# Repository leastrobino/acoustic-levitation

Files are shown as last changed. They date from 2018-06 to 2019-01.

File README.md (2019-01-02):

# Acoustic levitation

An acoustic levitation device designed as a daughterboard for the [DE0-Nano-SoC](http://www.terasic.com.tw/cgi-bin/page/archive.pl?Language=English&CategoryNo=165&No=941) (Terasic Inc.)

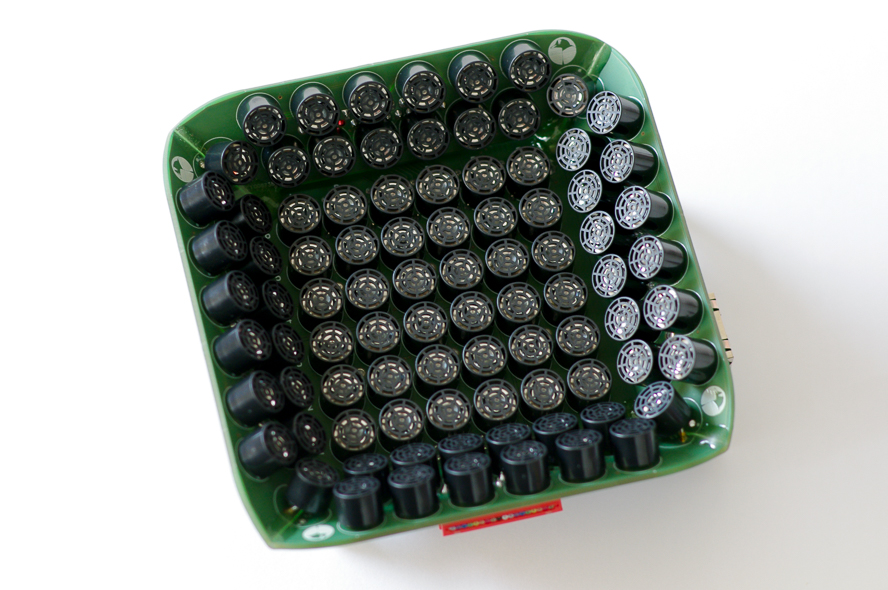
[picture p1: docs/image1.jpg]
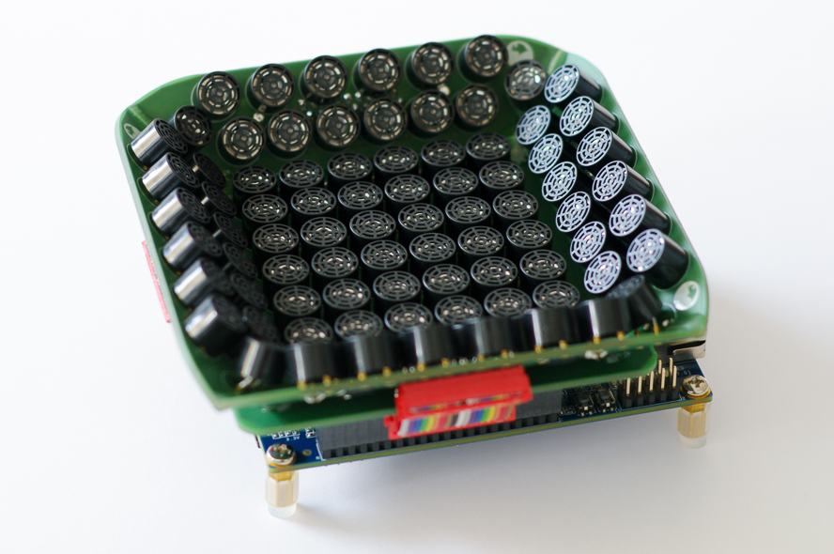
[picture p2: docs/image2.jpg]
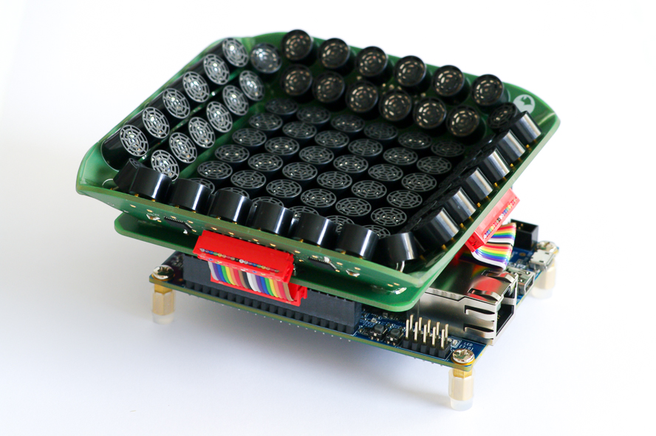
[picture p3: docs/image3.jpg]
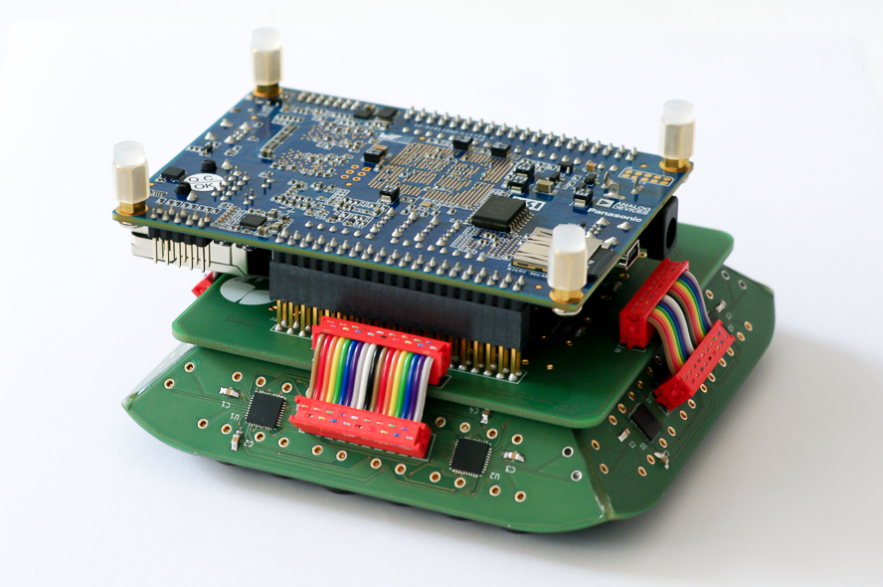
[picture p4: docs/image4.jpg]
[](https://leastrobino.github.io/acoustic-levitation/image1.jpg)[](https://leastrobino.github.io/acoustic-levitation/image2.jpg)[](https://leastrobino.github.io/acoustic-levitation/image3.jpg)[](https://leastrobino.github.io/acoustic-levitation/image4.jpg)

The piezoelectric transducers signals generation is written in VHDL. The phases computation and the G-Code interpreter are written in C and run on embedded Linux. The device controls 88 channels at 40 kHz with a phase resolution of π/625.

## Demonstration videos

#### Levitation of a 3 mm EPS particle in hand
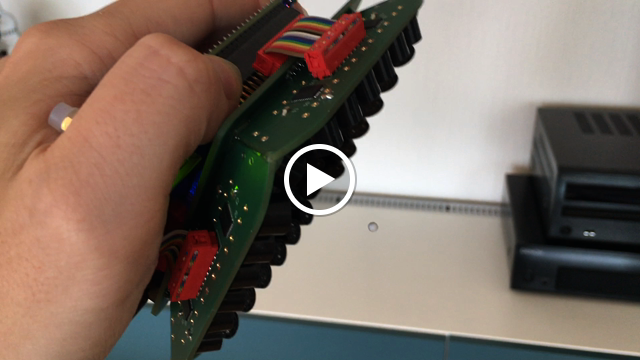
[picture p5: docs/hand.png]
Levitation device in hand


#### Up and down movements using G-Code
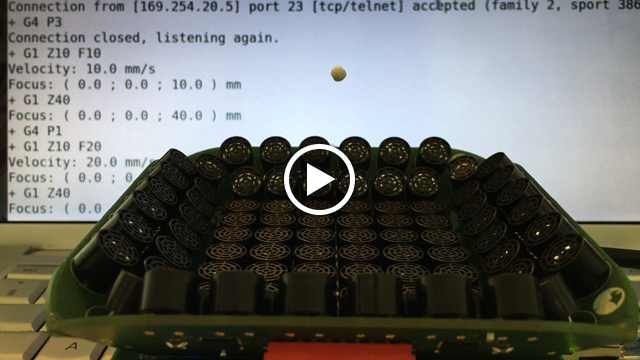
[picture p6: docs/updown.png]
Up and down movements


#### 2 mm EPS particle following a toolpath exported from FlatCAM
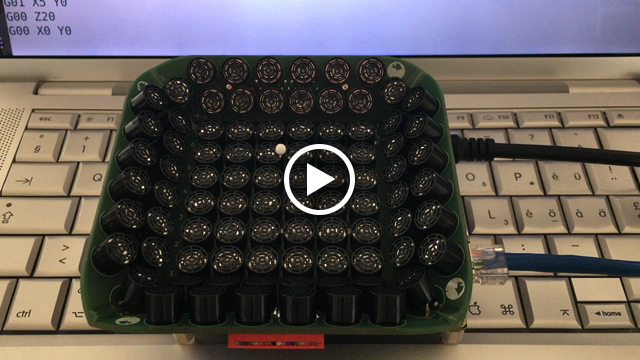
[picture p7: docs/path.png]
Particule following a path


Toolpath:

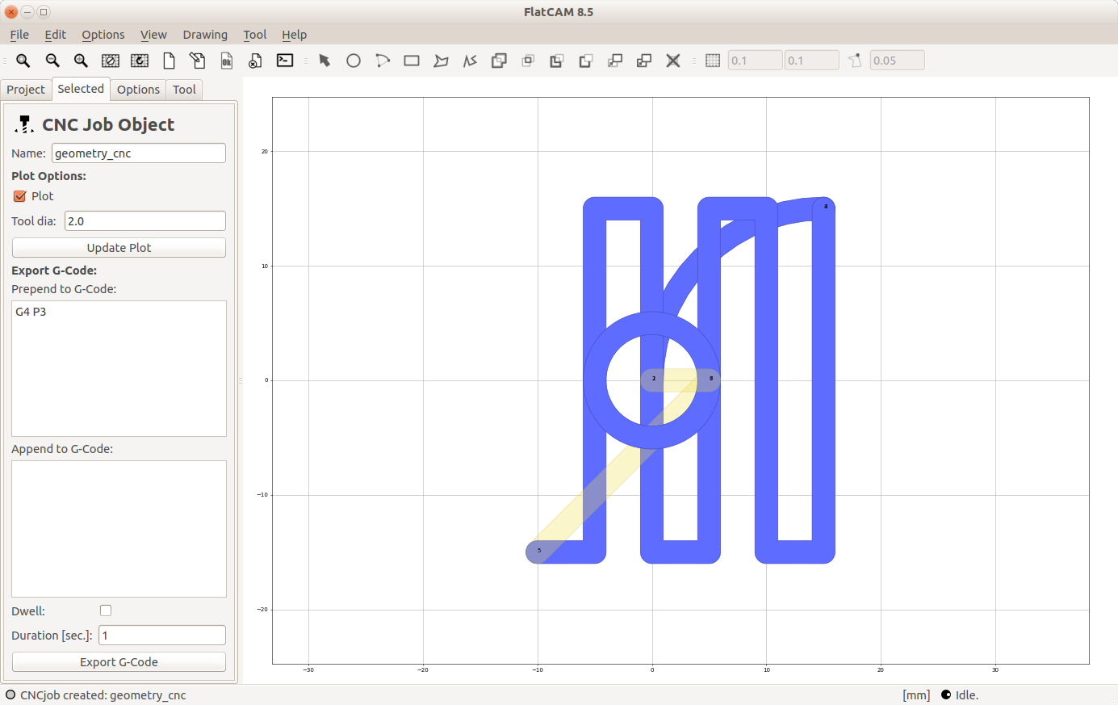
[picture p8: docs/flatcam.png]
Toolpath in FlatCAM
[](https://leastrobino.github.io/acoustic-levitation/flatcam.png)

## Bill of materials

| Quantity | Manufacturer           | Part number     |
| :------: | :--------------------- | :-------------- |
| 1        | CUI Inc.               | PJ-102AH        |
| 14       | Maxim Integrated       | MAX17079GTL+    |
| 88       | Murata                 | MA40S4S         |
| 2        | Samtec Inc.            | SSW-120-03-G-D  |
| 8        | TE Connectivity        | 8-215079-8      |
| 8        | TE Connectivity        | 8-215083-8      |
| 176      | TE Connectivity        | 8134-HC-8P2     |
| 1        | Traco Power            | TSR 2-2450      |
| 1        | Vishay Siliconix       | SI3421DV-T1-GE3 |
| 1        | Wurth Electronics Inc. | 61300111121     |
| 1        | Wurth Electronics Inc. | 61300811121     |
| 1        | Wurth Electronics Inc. | 61301011121     |
| 28       | Wurth Electronics Inc. | 885012207072    |

The PCBs were manufactured by [Eurocircuits](https://www.eurocircuits.com) (class 6D).

## License

This project is licensed under the [CERN OHL v1.2](LICENSE).

## References

1. A. Marzo, S. A. Seah, B. W. Drinkwater, D. R. Sahoo, B. Long, and S. Subramanian, *Holographic acoustic elements for manipulation of levitated objects*, Nature Communications 6, 8661, 2015.  
   <https://www.nature.com/articles/ncomms9661>
2. A. Marzo, *GauntLev: A Wearable to Manipulate Free-floating Objects*, Proceedings of the 2016 CHI Conference on Human Factors in Computing Systems (CHI '16), 3277-3281, 2016.  
   <https://dl.acm.org/citation.cfm?id=2858370>
3. A. Marzo, M. Caleap, and B. W. Drinkwater, *Acoustic Virtual Vortices with Tunable Orbital Angular Momentum for Trapping of Mie Particles*, Phys. Rev. Lett. 120, 044301, 2018.  
   <https://journals.aps.org/prl/abstract/10.1103/PhysRevLett.120.044301>
4. A. Künstner, *Lévitation acoustique*, Bachelor thesis, hepia, University of Applied Sciences Western Switzerland (HES-SO), Geneva, Switzerland, 2017.

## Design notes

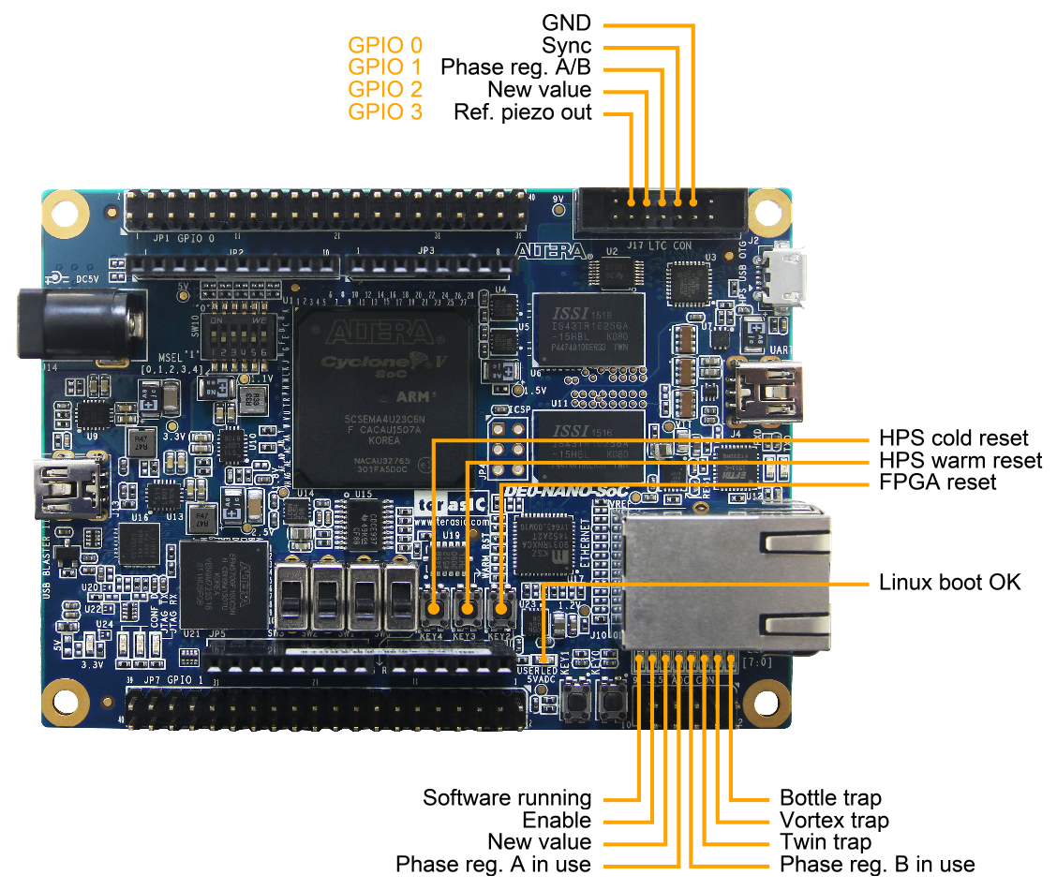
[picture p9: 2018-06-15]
docs/DE0-Nano-SoC_GPIO_LED_Buttons.png

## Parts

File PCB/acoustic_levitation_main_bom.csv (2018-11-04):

% Source: /Users/Lea/Documents/Acoustic levitation/PCB/acoustic_levitation_main.sch
% Date: Saturday, 03 November 2018 at 16:48:32
% Component count: 66
Reference | Quantity | Value | Footprint | Manufacturer | Manufacturer part number | Supplier 1 | Supplier part number 1 | Supplier 2 | Supplier part number 2
C1, C2, C3, C4, C5, C6, C7, C8, C9, C10, C11, C12 | 12 | 100n | C_0805_HandSoldering | Wurth Electronics Inc. | 885012207072 | Digi-Key | 732-8061-1-ND
J1 | 1 | DE0-Nano-SoC: GPIO 0 | Socket_Strip_Straight_2x20_Pitch2.54mm | Samtec Inc. | SSW-120-03-G-D | Digi-Key | SAM11959-ND
J2 | 1 | DE0-Nano-SoC: GPIO 1 | Socket_Strip_Straight_2x20_Pitch2.54mm | Samtec Inc. | SSW-120-03-G-D | Digi-Key | SAM11959-ND
J3 | 1 | DE0-Nano-SoC: JP3 | Pin_Header_Straight_1x08_Pitch2.54mm | Wurth Electronics Inc. | 61300811121 | Digi-Key | 732-5321-ND | Distrelec | 300-93-649
J4 | 1 | DE0-Nano-SoC: JP2 | Pin_Header_Straight_1x10_Pitch2.54mm | Wurth Electronics Inc. | 61301011121 | Digi-Key | 732-2670-ND | Distrelec | 300-93-651
J5 | 1 | DE0-Nano-SoC: JP5[3] | Pin_Header_Straight_1x01_Pitch2.54mm | Wurth Electronics Inc. | 61300111121 | Digi-Key | 732-5314-ND | Distrelec | 300-93-642
J6, J7, J8, J9 | 4 | 8-215079-8 | TE_8-215079-8 | TE Connectivity AMP Connectors | 8-215079-8 | Digi-Key | A99466CT-ND
J10 | 1 | PJ-102AH | CUI_PJ-102AH | CUI Inc. | PJ-102AH | Digi-Key | CP-102AH-ND
Q1 | 1 | Si3421DV | TSOP-6_2.9x1.5mm_Pitch0.95mm | Vishay Siliconix | SI3421DV-T1-GE3 | Digi-Key | SI3421DV-T1-GE3CT-ND
TR1, TR2, TR3, TR4, TR5, TR6, TR7, TR8, TR9, TR10, TR11, TR12, TR13, TR14, TR15, TR16, TR17, TR18, TR19, TR20, TR21, TR22, TR23, TR24, TR25, TR26, TR27, TR28, TR29, TR30, TR31, TR32, TR33, TR34, TR35, TR36 | 36 | MA40S4S | Murata_MA40S4S_TE_8134-HC-8P2 | Murata | MA40S4S | Digi-Key | 490-7707-ND
U1, U2, U3, U4, U5, U6 | 6 | MAX17079 | QFN-40-1EP_6x6mm_Pitch0.5mm_HandSoldering | Maxim Integrated | MAX17079GTL+ | Digi-Key | MAX17079GTL+-ND
U7 | 1 | TSR2-2450 | Traco_TSR2 | Traco Power | TSR 2-2450 | Mouser | 495-TSR2-2450 | Distrelec | 300-67-301

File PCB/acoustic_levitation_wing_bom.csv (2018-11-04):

% Source: /Users/Lea/Documents/Acoustic levitation/PCB/acoustic_levitation_wing.sch
% Date: Saturday, 03 November 2018 at 16:48:45
% Component count: 21
Reference | Quantity | Value | Footprint | Manufacturer | Manufacturer part number | Supplier 1 | Supplier part number 1 | Supplier 2 | Supplier part number 2
C1, C2, C3, C4 | 4 | 100n | C_0805_HandSoldering | Wurth Electronics Inc. | 885012207072 | Digi-Key | 732-8061-1-ND
J1 | 1 | 8-215079-8 | TE_8-215079-8 | TE Connectivity AMP Connectors | 8-215079-8 | Digi-Key | A99466CT-ND
TR1, TR2, TR3, TR4, TR5, TR6, TR7, TR8, TR9, TR10, TR11, TR12, TR13, TR14 | 14 | MA40S4S | Murata_MA40S4S_TE_8134-HC-8P2 | Murata | MA40S4S | Digi-Key | 490-7707-ND
U1, U2 | 2 | MAX17079 | QFN-40-1EP_6x6mm_Pitch0.5mm_HandSoldering | Maxim Integrated | MAX17079GTL+ | Digi-Key | MAX17079GTL+-ND

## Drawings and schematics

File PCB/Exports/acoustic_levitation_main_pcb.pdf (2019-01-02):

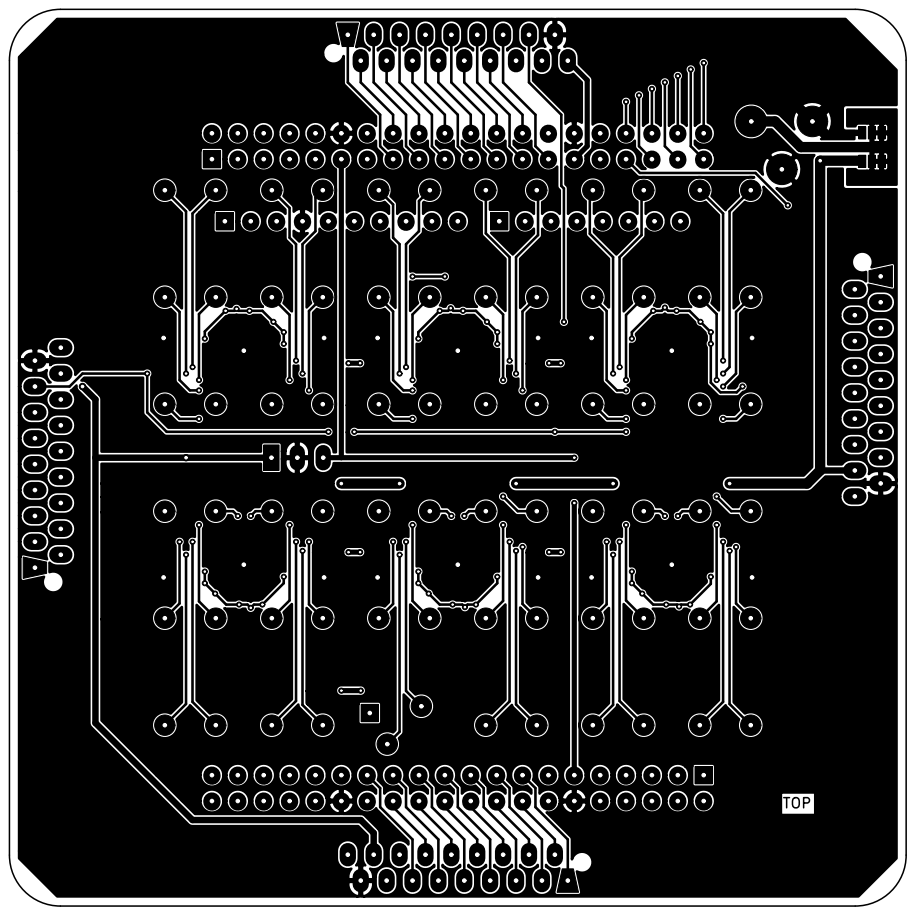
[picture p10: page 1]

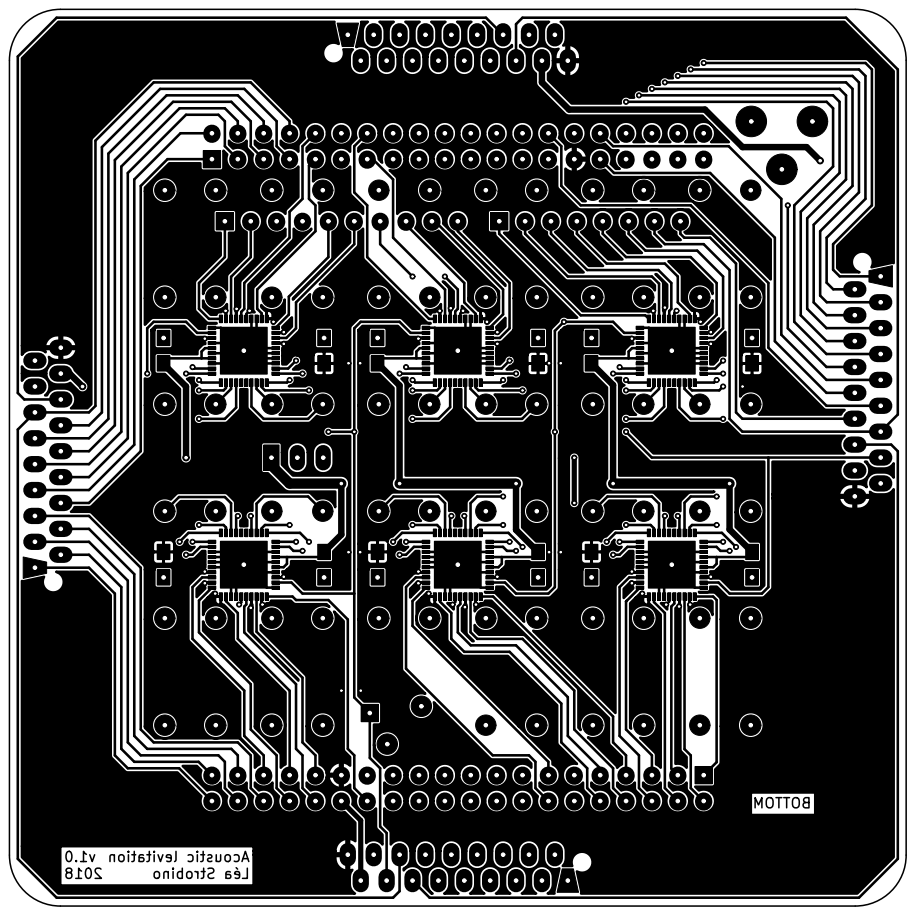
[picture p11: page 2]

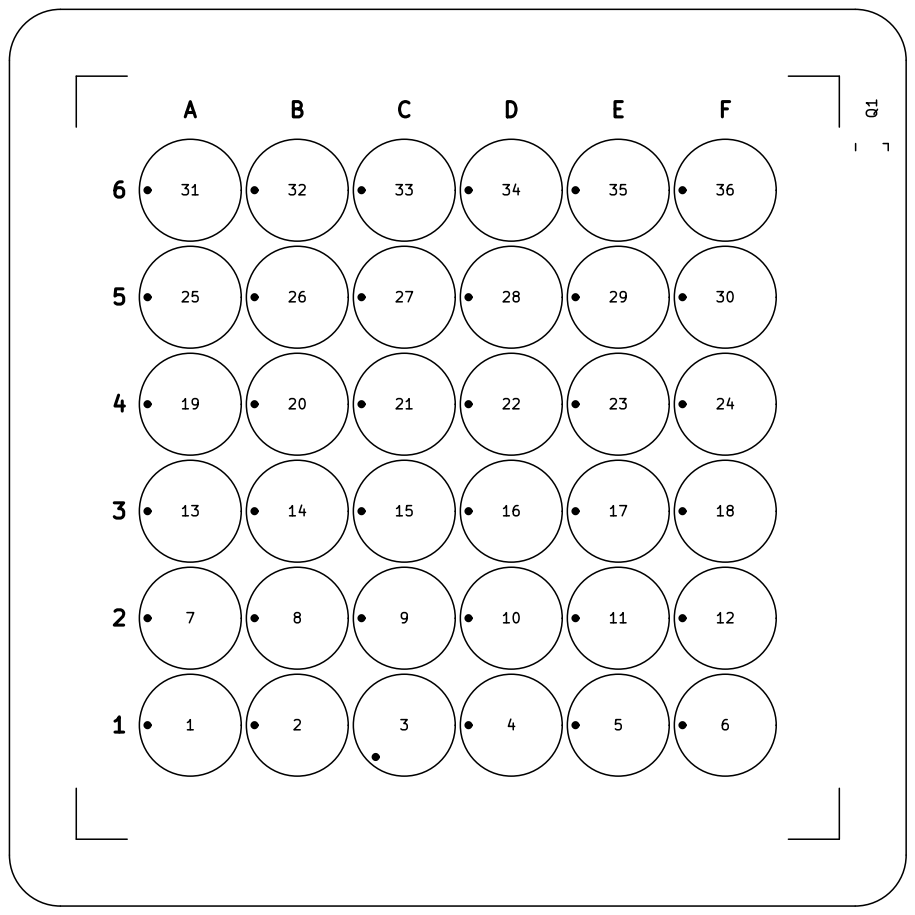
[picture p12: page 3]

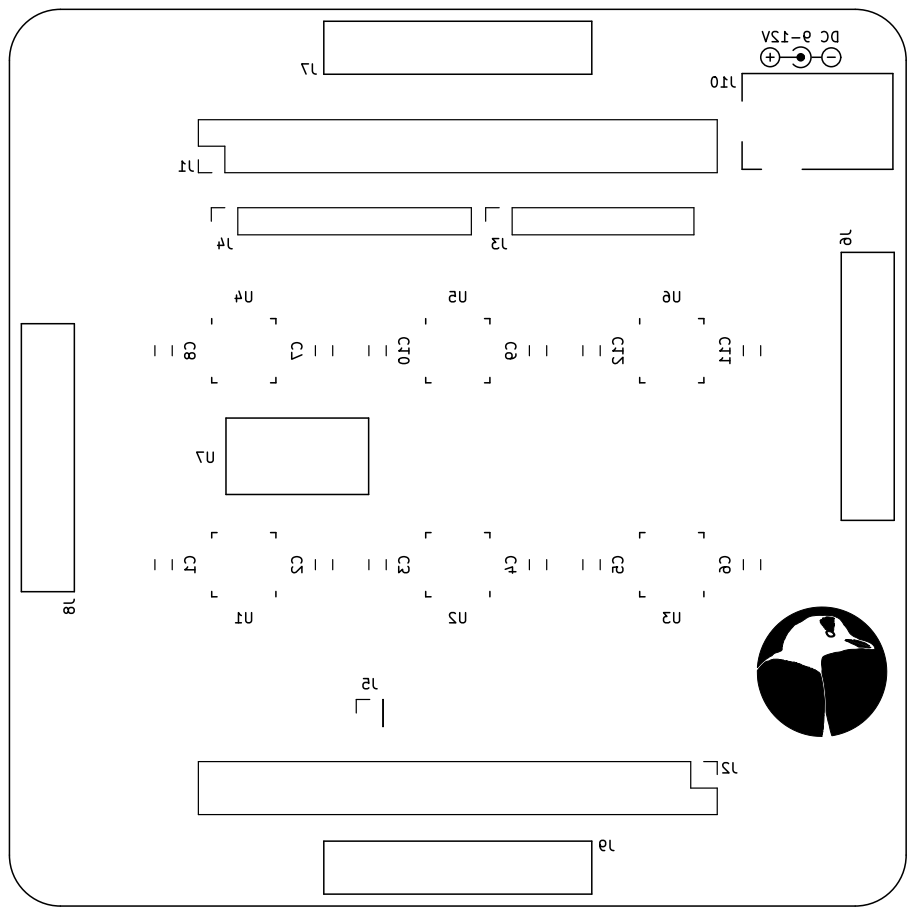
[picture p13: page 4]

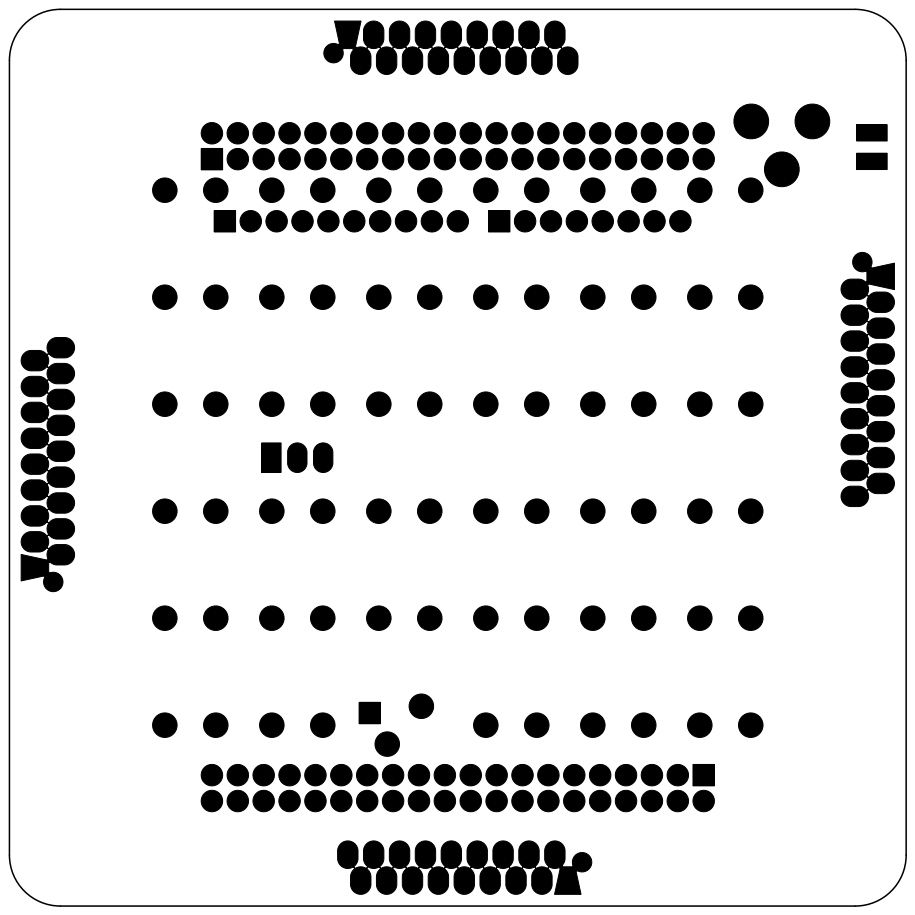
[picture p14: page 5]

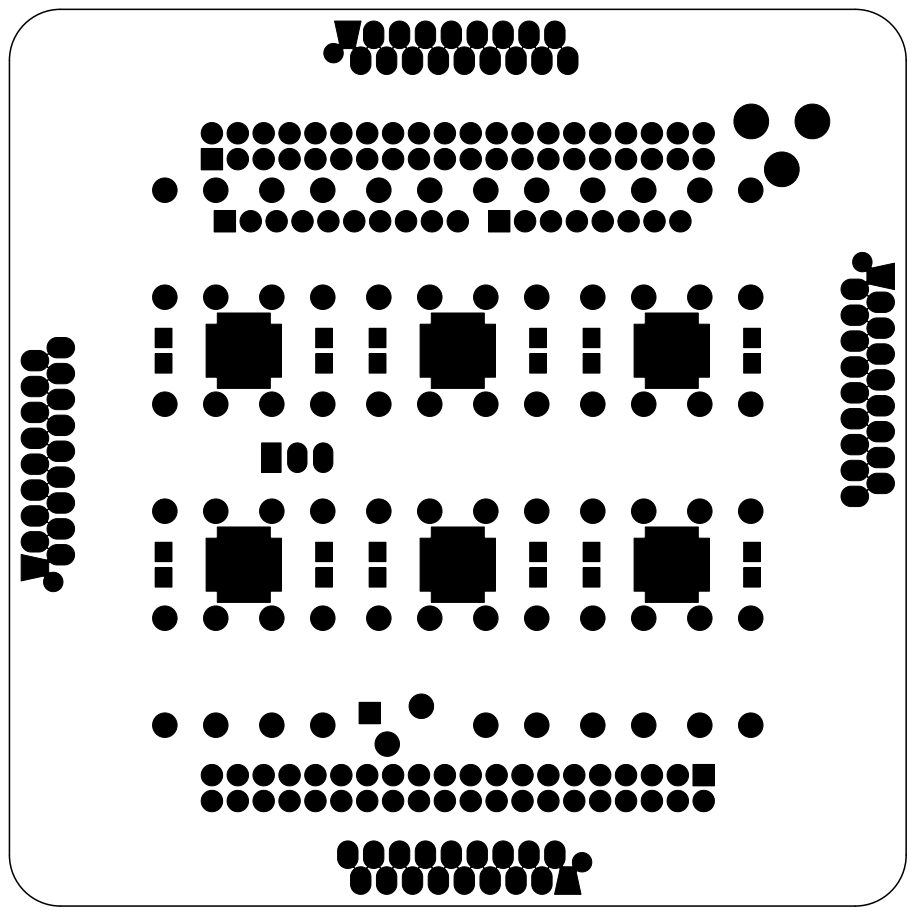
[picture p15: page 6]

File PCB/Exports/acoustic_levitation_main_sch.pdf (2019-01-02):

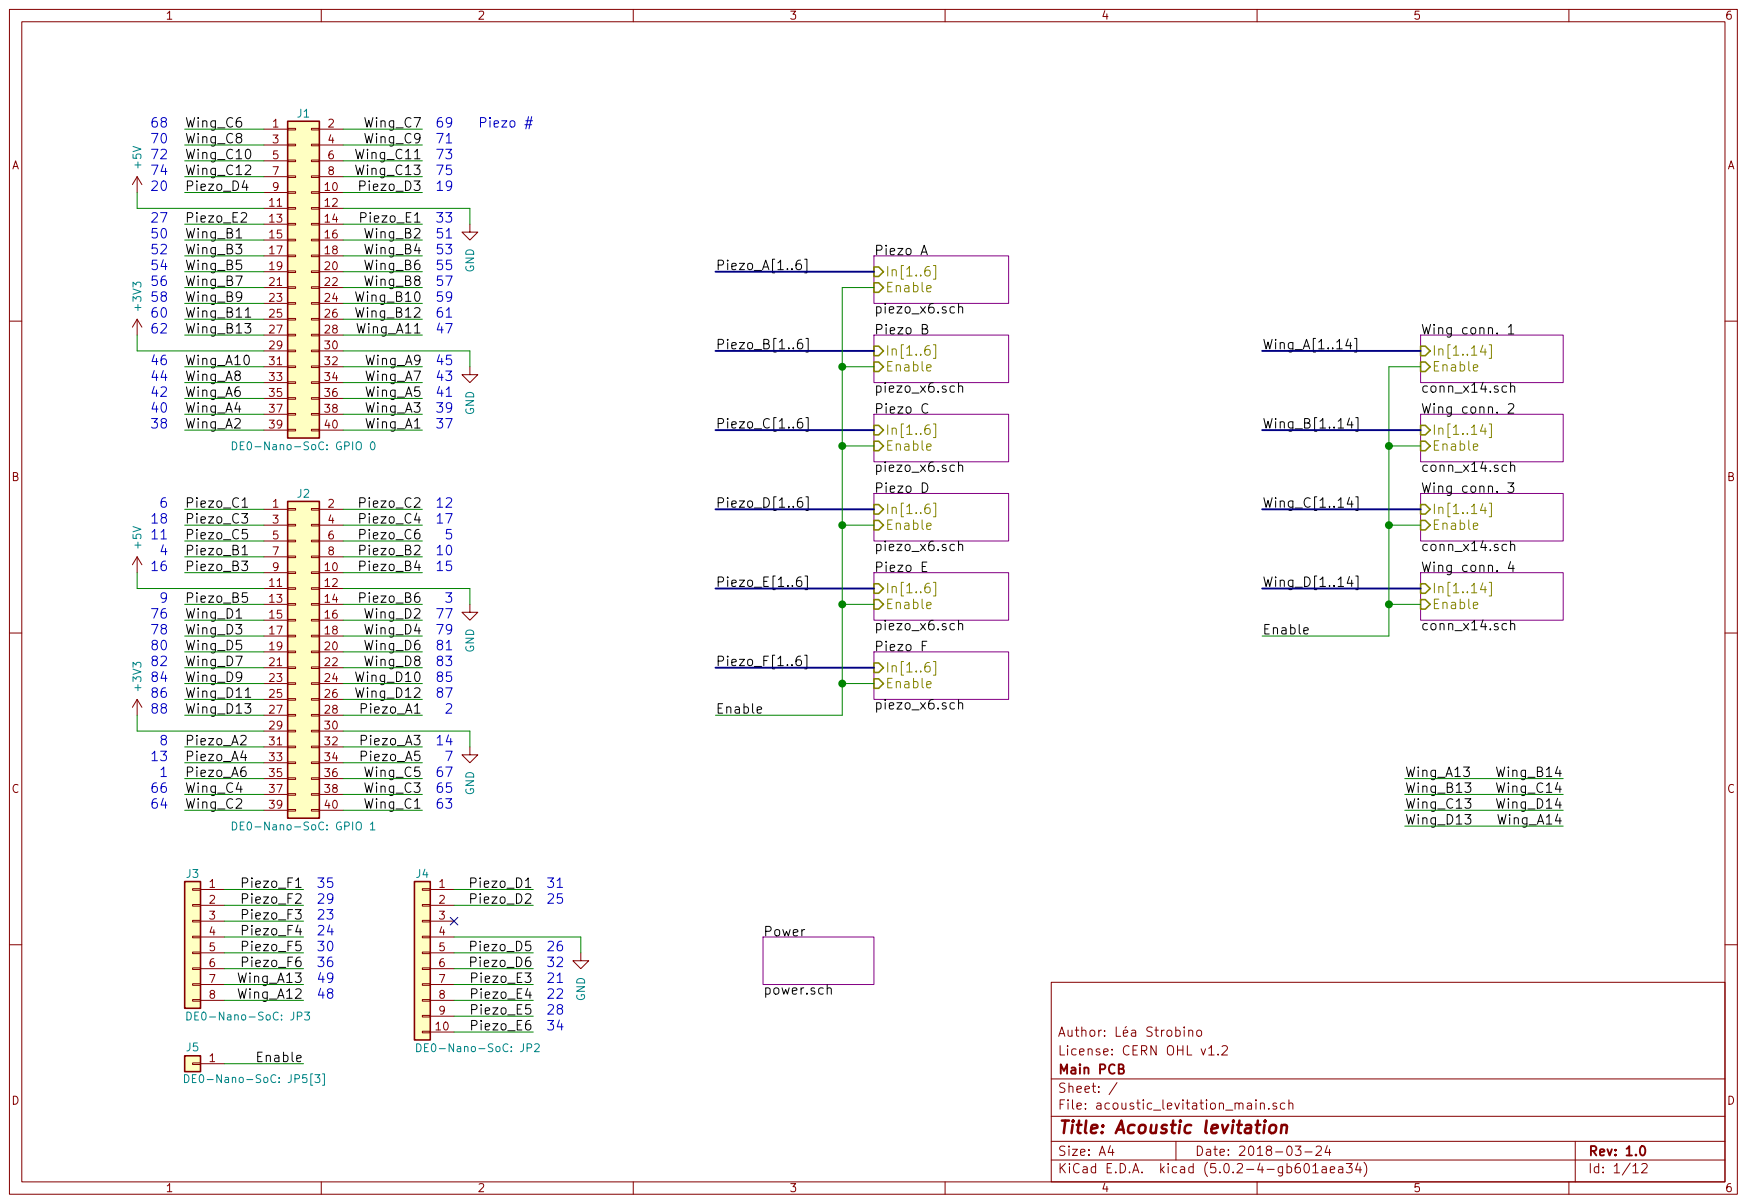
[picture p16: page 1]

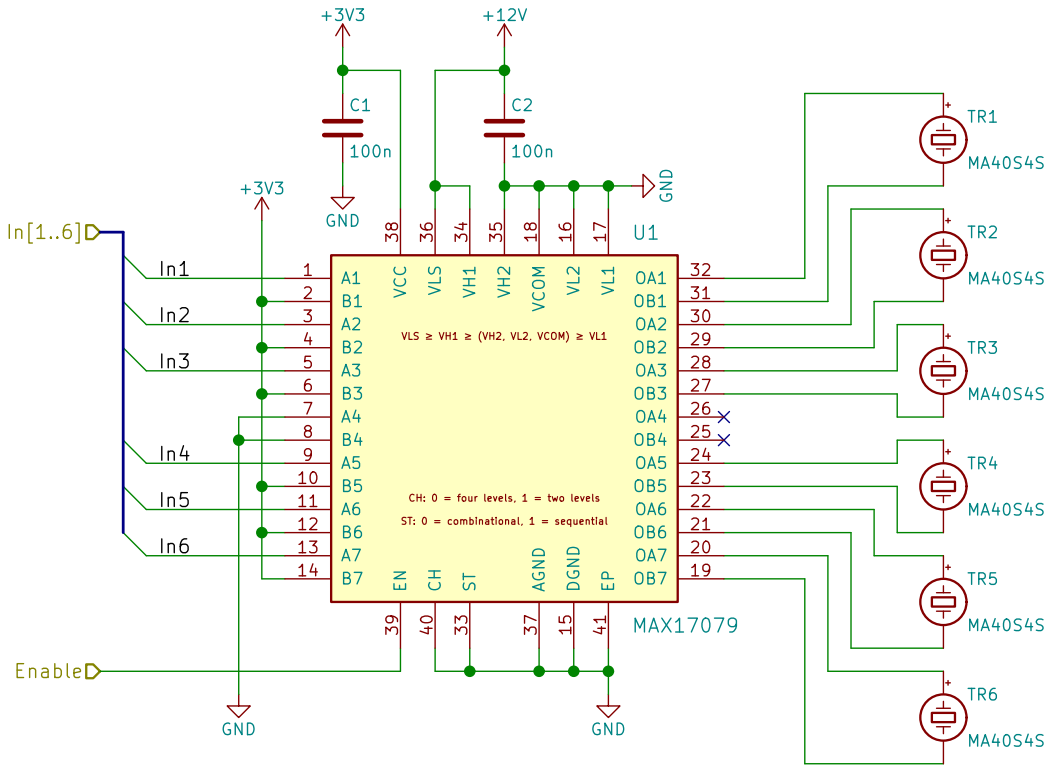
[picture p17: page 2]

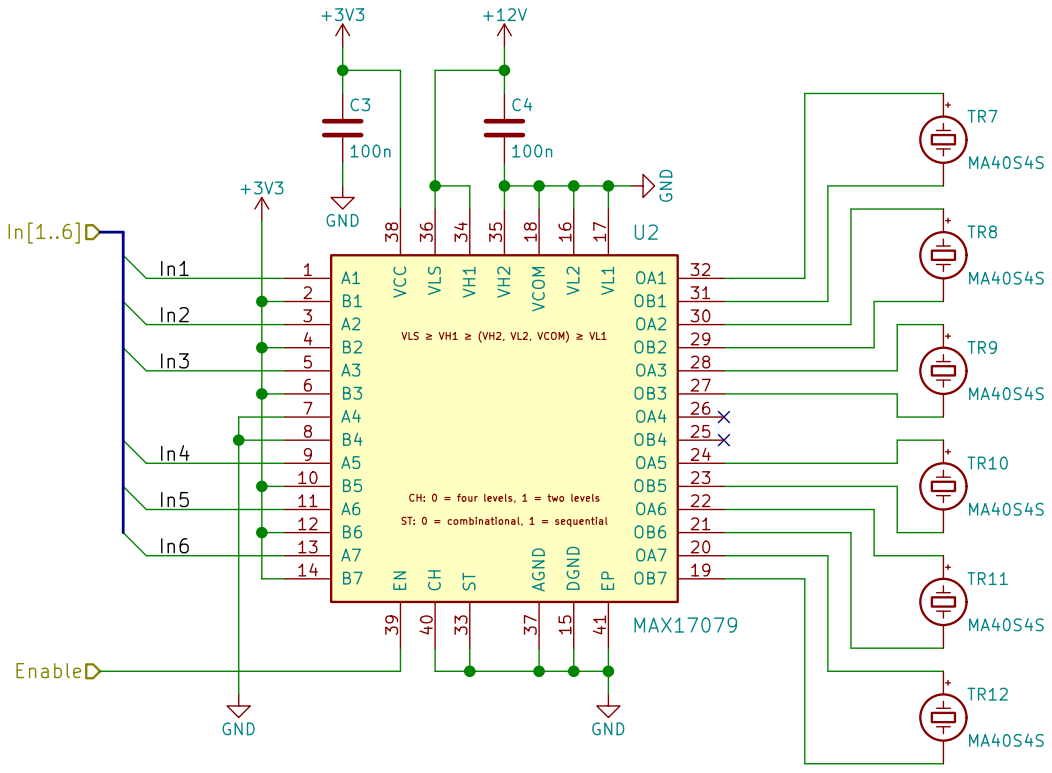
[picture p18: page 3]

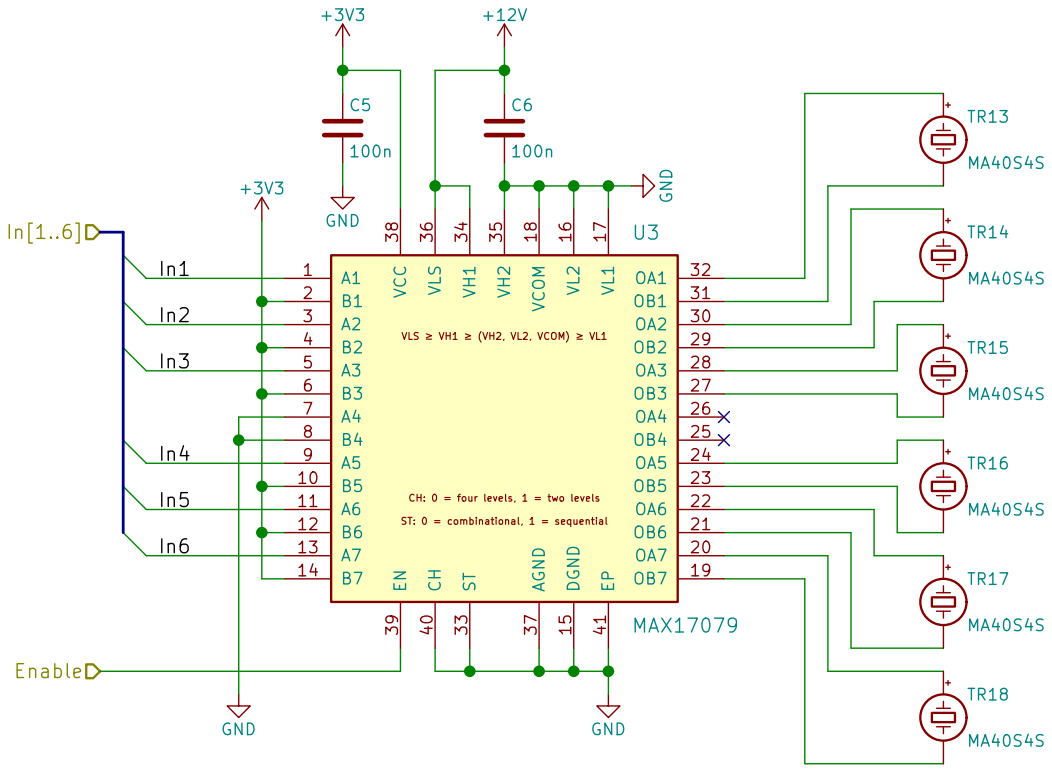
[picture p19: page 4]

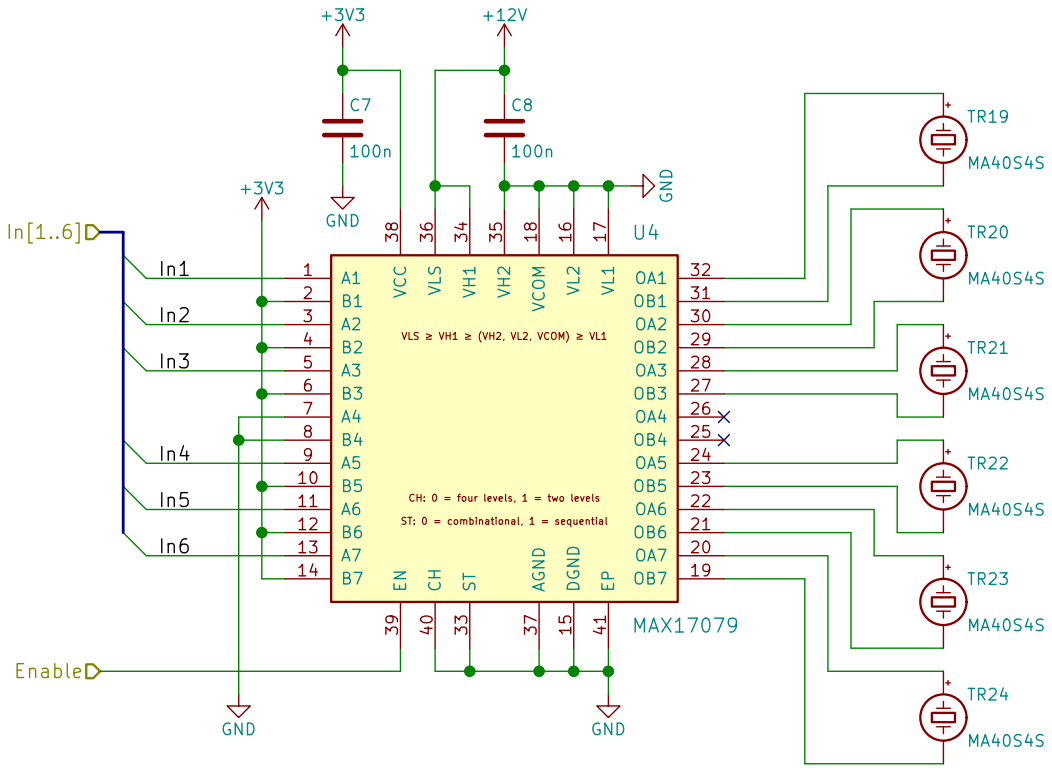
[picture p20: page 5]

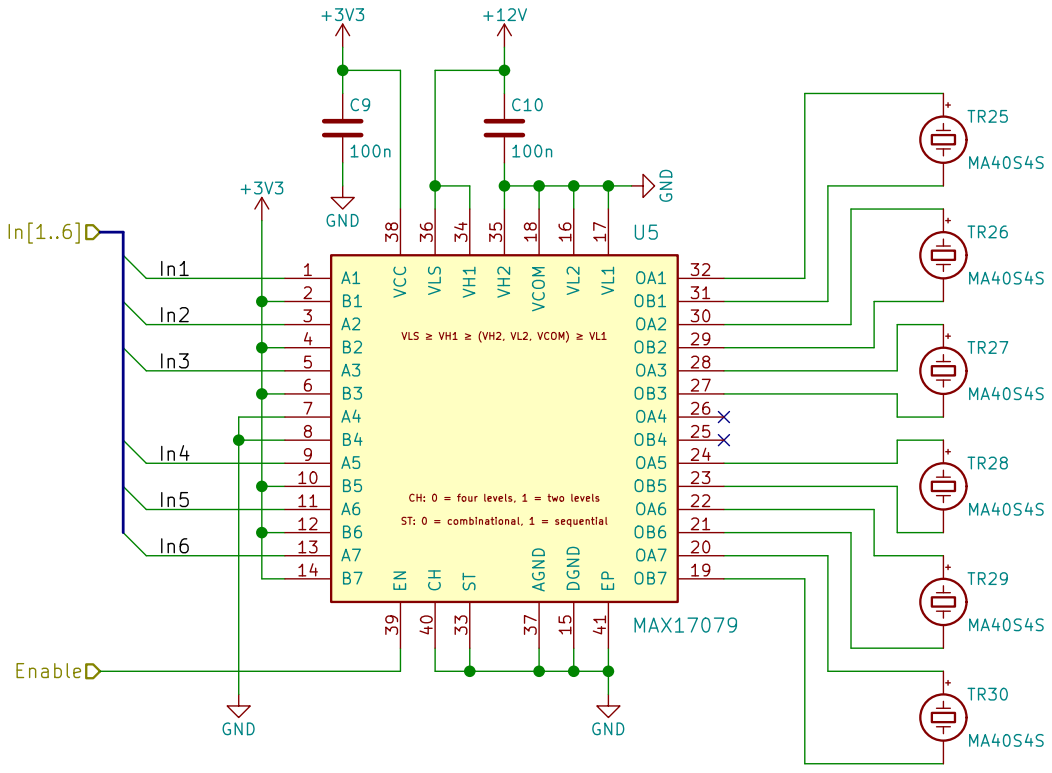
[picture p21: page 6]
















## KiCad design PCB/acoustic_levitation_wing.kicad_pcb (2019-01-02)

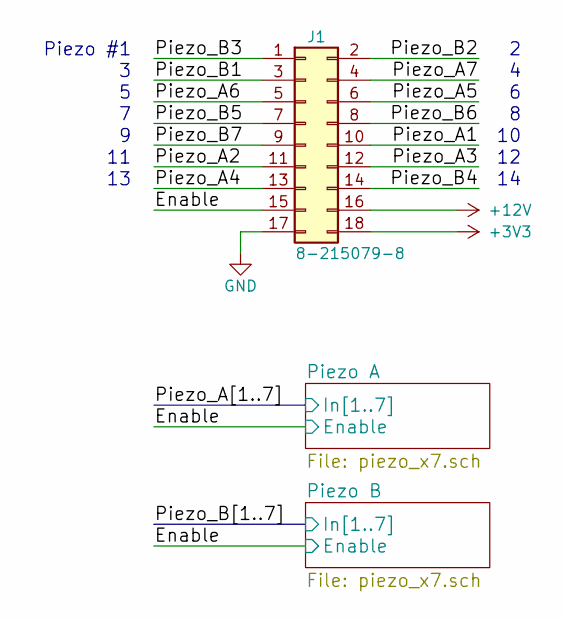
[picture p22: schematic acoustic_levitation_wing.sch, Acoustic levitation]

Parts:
J1: 8-215079-8; TE_8-215079-8; ManufacturerPartNumber 8-215079-8

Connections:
+3V3: J1.18; also elsewhere on the board
+12V: J1.16; also elsewhere on the board
/Enable: J1.15; also elsewhere on the board
/Piezo_A1: J1.10; also elsewhere on the board
/Piezo_A2: J1.11; also elsewhere on the board
/Piezo_A3: J1.12; also elsewhere on the board
/Piezo_A4: J1.13; also elsewhere on the board
/Piezo_A5: J1.6; also elsewhere on the board
/Piezo_A6: J1.5; also elsewhere on the board
/Piezo_A7: J1.4; also elsewhere on the board
/Piezo_B1: J1.3; also elsewhere on the board
/Piezo_B2: J1.2; also elsewhere on the board
/Piezo_B3: J1.1; also elsewhere on the board
/Piezo_B4: J1.14; also elsewhere on the board
/Piezo_B5: J1.7; also elsewhere on the board
/Piezo_B6: J1.8; also elsewhere on the board
/Piezo_B7: J1.9; also elsewhere on the board
GND: J1.17; also elsewhere on the board

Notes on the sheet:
Piezo #1

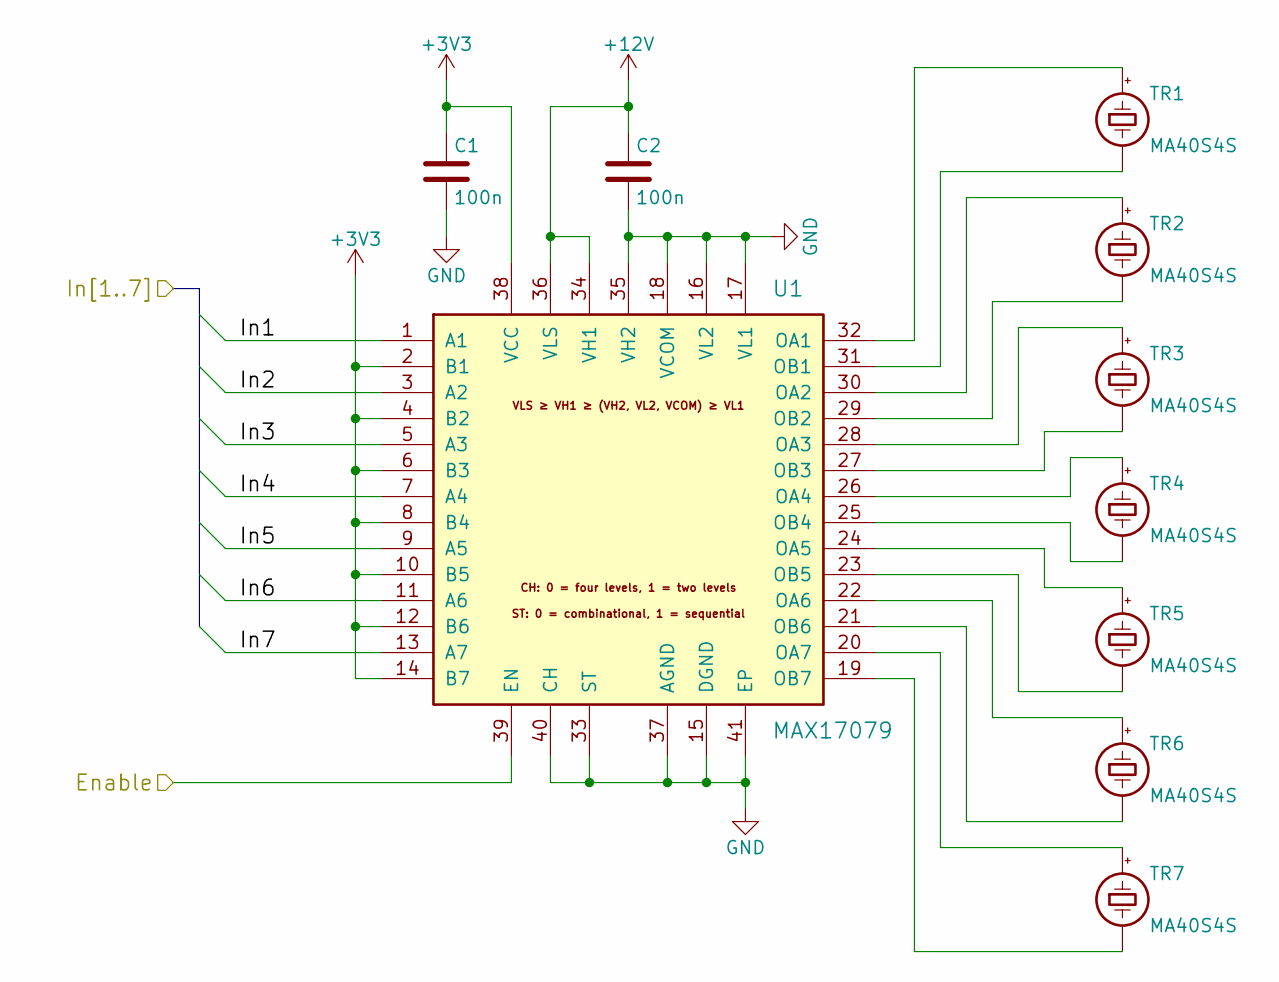
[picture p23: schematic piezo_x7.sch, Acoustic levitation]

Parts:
C1, C2: 100n; C_0805_HandSoldering; ManufacturerPartNumber 885012207072
TR1, TR2, TR3, TR4, TR5, TR6, TR7: MA40S4S; Murata_MA40S4S_TE_8134-HC-8P2; ManufacturerPartNumber MA40S4S
U1: MAX17079; QFN-40-1EP_6x6mm_Pitch0.5mm_HandSoldering; ManufacturerPartNumber MAX17079GTL+

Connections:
+3V3: C1.1, U1.2 (B1), U1.4 (B2), U1.6 (B3), U1.8 (B4), U1.10 (B5), U1.12 (B6), U1.14 (B7), U1.38 (VCC); also elsewhere on the board
+12V: C2.1, U1.34 (VH1), U1.36 (VLS); also elsewhere on the board
/Enable: U1.39 (EN); also elsewhere on the board
/Piezo_A1: U1.1 (A1); also elsewhere on the board
/Piezo_A2: U1.3 (A2); also elsewhere on the board
/Piezo_A3: U1.5 (A3); also elsewhere on the board
/Piezo_A4: U1.7 (A4); also elsewhere on the board
/Piezo_A5: U1.9 (A5); also elsewhere on the board
/Piezo_A6: U1.11 (A6); also elsewhere on the board
/Piezo_A7: U1.13 (A7); also elsewhere on the board
GND: C1.2, C2.2, U1.15 (DGND), U1.16 (VL2), U1.17 (VL1), U1.18 (VCOM), U1.33 (ST), U1.35 (VH2), U1.37 (AGND), U1.40 (CH), U1.41 (EP); also elsewhere on the board
unnamed: TR1.1 (-), U1.31 (OB1)
unnamed: TR1.2 (+), U1.32 (OA1)
unnamed: TR2.1 (-), U1.29 (OB2)
unnamed: TR2.2 (+), U1.30 (OA2)
unnamed: TR3.1 (-), U1.27 (OB3)
unnamed: TR3.2 (+), U1.28 (OA3)
unnamed: TR4.1 (-), U1.25 (OB4)
unnamed: TR4.2 (+), U1.26 (OA4)
unnamed: TR5.1 (-), U1.23 (OB5)
unnamed: TR5.2 (+), U1.24 (OA5)
unnamed: TR6.1 (-), U1.21 (OB6)
unnamed: TR6.2 (+), U1.22 (OA6)
unnamed: TR7.1 (-), U1.19 (OB7)
unnamed: TR7.2 (+), U1.20 (OA7)

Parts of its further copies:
C3, C4: 100n; C_0805_HandSoldering; ManufacturerPartNumber 885012207072
TR8, TR9, TR10, TR11, TR12, TR13, TR14: MA40S4S; Murata_MA40S4S_TE_8134-HC-8P2; ManufacturerPartNumber MA40S4S
U2: MAX17079; QFN-40-1EP_6x6mm_Pitch0.5mm_HandSoldering; ManufacturerPartNumber MAX17079GTL+

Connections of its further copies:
+3V3: C3.1, U2.2 (B1), U2.4 (B2), U2.6 (B3), U2.8 (B4), U2.10 (B5), U2.12 (B6), U2.14 (B7), U2.38 (VCC); also elsewhere on the board
+12V: C4.1, U2.34 (VH1), U2.36 (VLS); also elsewhere on the board
/Enable: U2.39 (EN); also elsewhere on the board
/Piezo_B1: U2.1 (A1); also elsewhere on the board
/Piezo_B2: U2.3 (A2); also elsewhere on the board
/Piezo_B3: U2.5 (A3); also elsewhere on the board
/Piezo_B4: U2.7 (A4); also elsewhere on the board
/Piezo_B5: U2.9 (A5); also elsewhere on the board
/Piezo_B6: U2.11 (A6); also elsewhere on the board
/Piezo_B7: U2.13 (A7); also elsewhere on the board
GND: C3.2, C4.2, U2.15 (DGND), U2.16 (VL2), U2.17 (VL1), U2.18 (VCOM), U2.33 (ST), U2.35 (VH2), U2.37 (AGND), U2.40 (CH), U2.41 (EP); also elsewhere on the board
unnamed: TR8.1 (-), U2.31 (OB1)
unnamed: TR8.2 (+), U2.32 (OA1)
unnamed: TR9.1 (-), U2.29 (OB2)
unnamed: TR9.2 (+), U2.30 (OA2)
unnamed: TR10.1 (-), U2.27 (OB3)
unnamed: TR10.2 (+), U2.28 (OA3)
unnamed: TR11.1 (-), U2.25 (OB4)
unnamed: TR11.2 (+), U2.26 (OA4)
unnamed: TR12.1 (-), U2.23 (OB5)
unnamed: TR12.2 (+), U2.24 (OA5)
unnamed: TR13.1 (-), U2.21 (OB6)
unnamed: TR13.2 (+), U2.22 (OA6)
unnamed: TR14.1 (-), U2.19 (OB7)
unnamed: TR14.2 (+), U2.20 (OA7)

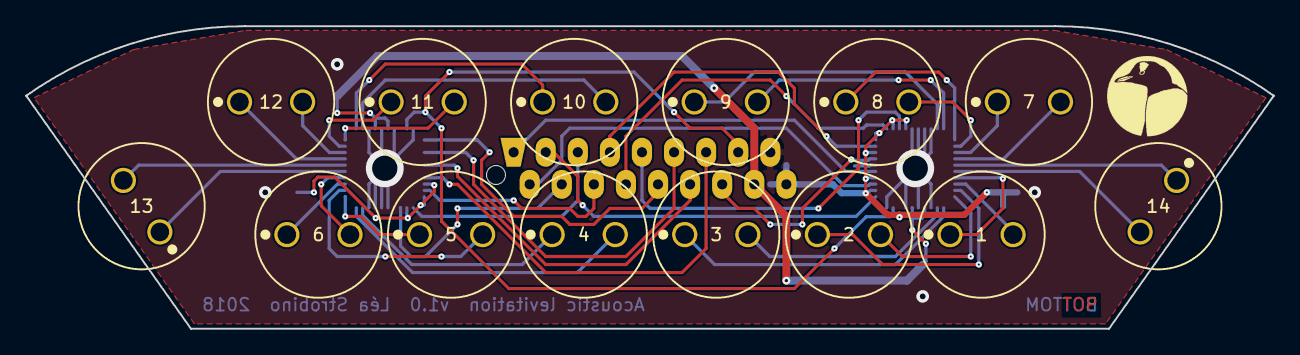
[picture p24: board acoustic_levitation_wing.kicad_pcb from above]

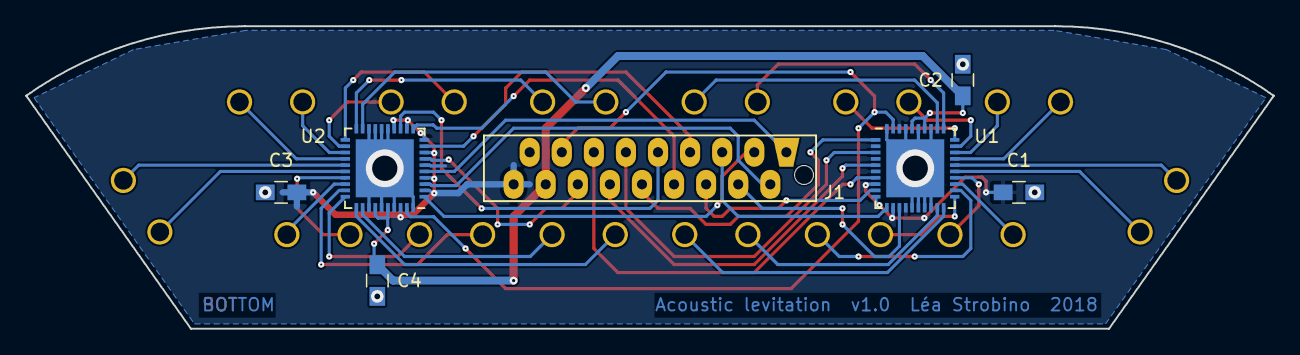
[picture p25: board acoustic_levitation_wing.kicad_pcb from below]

Board: 2 copper layers, 98.8 x 24.0 mm, 21 parts (7 on the bottom side), 46 nets.

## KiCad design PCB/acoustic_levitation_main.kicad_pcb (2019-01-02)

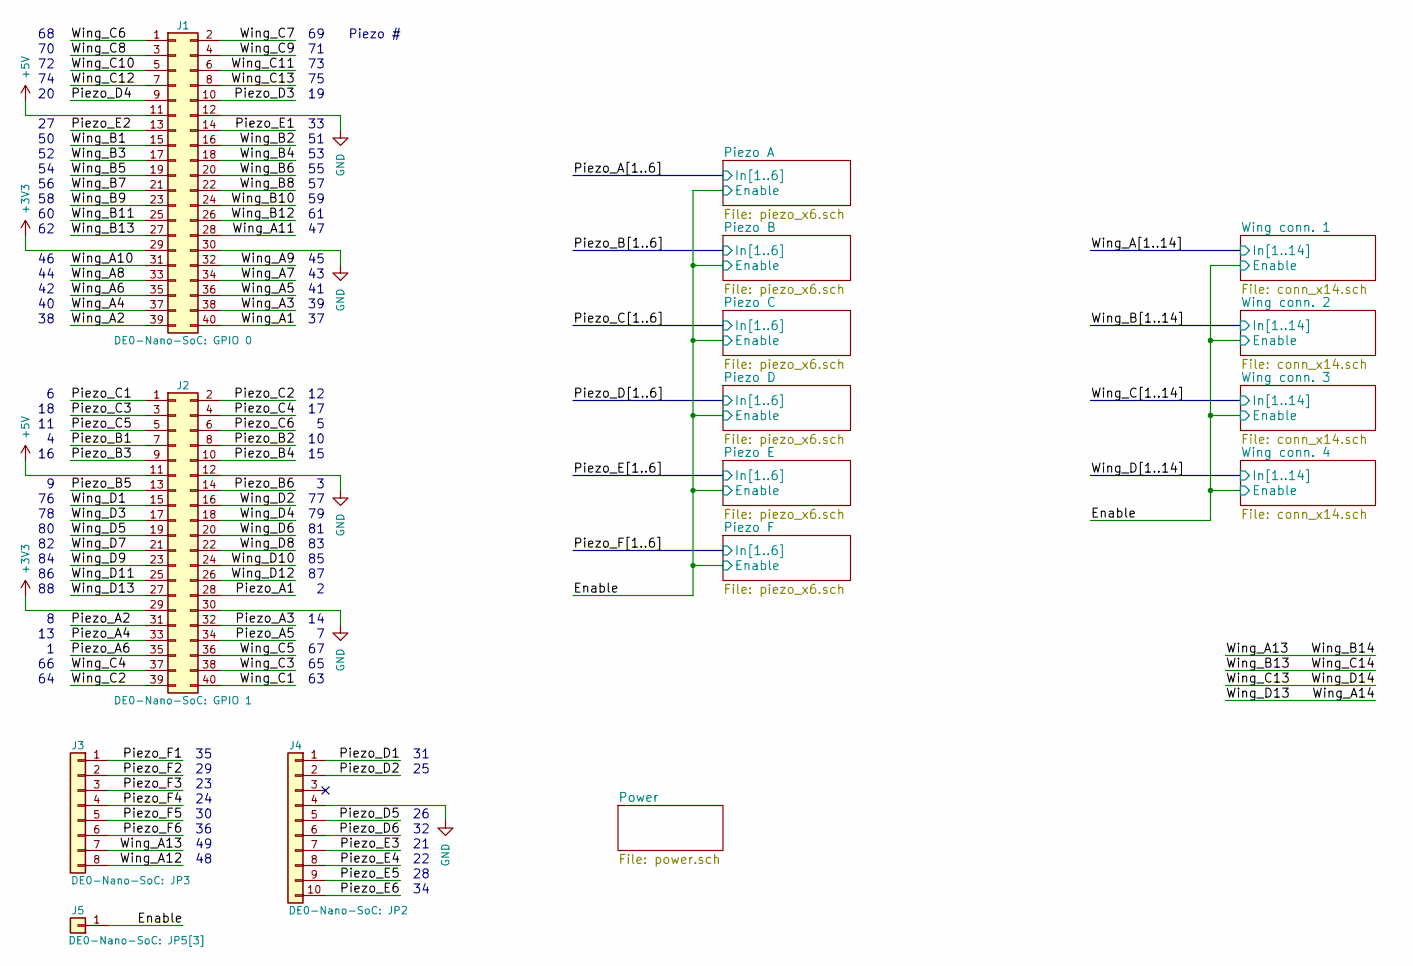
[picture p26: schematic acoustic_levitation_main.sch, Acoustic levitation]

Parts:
J1: DE0-Nano-SoC: GPIO 0; Socket_Strip_Straight_2x20_Pitch2.54mm; ManufacturerPartNumber SSW-120-03-G-D
J2: DE0-Nano-SoC: GPIO 1; Socket_Strip_Straight_2x20_Pitch2.54mm; ManufacturerPartNumber SSW-120-03-G-D
J3: DE0-Nano-SoC: JP3; Pin_Header_Straight_1x08_Pitch2.54mm; ManufacturerPartNumber 61300811121
J4: DE0-Nano-SoC: JP2; Pin_Header_Straight_1x10_Pitch2.54mm; ManufacturerPartNumber 61301011121
J5: DE0-Nano-SoC: JP5[3]; Pin_Header_Straight_1x01_Pitch2.54mm; ManufacturerPartNumber 61300111121

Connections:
+3V3: J1.29, J2.29; also elsewhere on the board
+5V: J1.11, J2.11; also elsewhere on the board
/Enable: J5.1; also elsewhere on the board
/Piezo_A1: J2.28; also elsewhere on the board
/Piezo_A2: J2.31; also elsewhere on the board
/Piezo_A3: J2.32; also elsewhere on the board
/Piezo_A4: J2.33; also elsewhere on the board
/Piezo_A5: J2.34; also elsewhere on the board
/Piezo_A6: J2.35; also elsewhere on the board
/Piezo_B1: J2.7; also elsewhere on the board
/Piezo_B2: J2.8; also elsewhere on the board
/Piezo_B3: J2.9; also elsewhere on the board
/Piezo_B4: J2.10; also elsewhere on the board
/Piezo_B5: J2.13; also elsewhere on the board
/Piezo_B6: J2.14; also elsewhere on the board
/Piezo_C1: J2.1; also elsewhere on the board
/Piezo_C2: J2.2; also elsewhere on the board
/Piezo_C3: J2.3; also elsewhere on the board
/Piezo_C4: J2.4; also elsewhere on the board
/Piezo_C5: J2.5; also elsewhere on the board
/Piezo_C6: J2.6; also elsewhere on the board
/Piezo_D1: J4.1; also elsewhere on the board
/Piezo_D2: J4.2; also elsewhere on the board
/Piezo_D3: J1.10; also elsewhere on the board
/Piezo_D4: J1.9; also elsewhere on the board
/Piezo_D5: J4.5; also elsewhere on the board
/Piezo_D6: J4.6; also elsewhere on the board
/Piezo_E1: J1.14; also elsewhere on the board
/Piezo_E2: J1.13; also elsewhere on the board
/Piezo_E3: J4.7; also elsewhere on the board
/Piezo_E4: J4.8; also elsewhere on the board
/Piezo_E5: J4.9; also elsewhere on the board
/Piezo_E6: J4.10; also elsewhere on the board
/Piezo_F1: J3.1; also elsewhere on the board
/Piezo_F2: J3.2; also elsewhere on the board
/Piezo_F3: J3.3; also elsewhere on the board
/Piezo_F4: J3.4; also elsewhere on the board
/Piezo_F5: J3.5; also elsewhere on the board
/Piezo_F6: J3.6; also elsewhere on the board
/Wing_A1: J1.40; also elsewhere on the board
/Wing_A2: J1.39; also elsewhere on the board
/Wing_A3: J1.38; also elsewhere on the board
/Wing_A4: J1.37; also elsewhere on the board
/Wing_A5: J1.36; also elsewhere on the board
/Wing_A6: J1.35; also elsewhere on the board
/Wing_A7: J1.34; also elsewhere on the board
/Wing_A8: J1.33; also elsewhere on the board
/Wing_A9: J1.32; also elsewhere on the board
/Wing_A10: J1.31; also elsewhere on the board
/Wing_A11: J1.28; also elsewhere on the board
/Wing_A12: J3.8; also elsewhere on the board
/Wing_A13: J3.7; also elsewhere on the board
/Wing_A14: J2.27; also elsewhere on the board
/Wing_B1: J1.15; also elsewhere on the board
/Wing_B2: J1.16; also elsewhere on the board
/Wing_B3: J1.17; also elsewhere on the board
/Wing_B4: J1.18; also elsewhere on the board
/Wing_B5: J1.19; also elsewhere on the board
/Wing_B6: J1.20; also elsewhere on the board
/Wing_B7: J1.21; also elsewhere on the board
/Wing_B8: J1.22; also elsewhere on the board
/Wing_B9: J1.23; also elsewhere on the board
/Wing_B10: J1.24; also elsewhere on the board
/Wing_B11: J1.25; also elsewhere on the board
/Wing_B12: J1.26; also elsewhere on the board
/Wing_B13: J1.27; also elsewhere on the board
/Wing_C1: J2.40; also elsewhere on the board
/Wing_C2: J2.39; also elsewhere on the board
/Wing_C3: J2.38; also elsewhere on the board
/Wing_C4: J2.37; also elsewhere on the board
/Wing_C5: J2.36; also elsewhere on the board
/Wing_C6: J1.1; also elsewhere on the board
/Wing_C7: J1.2; also elsewhere on the board
/Wing_C8: J1.3; also elsewhere on the board
/Wing_C9: J1.4; also elsewhere on the board
/Wing_C10: J1.5; also elsewhere on the board
/Wing_C11: J1.6; also elsewhere on the board
/Wing_C12: J1.7; also elsewhere on the board
/Wing_C13: J1.8; also elsewhere on the board
/Wing_D1: J2.15; also elsewhere on the board
/Wing_D2: J2.16; also elsewhere on the board
/Wing_D3: J2.17; also elsewhere on the board
/Wing_D4: J2.18; also elsewhere on the board
/Wing_D5: J2.19; also elsewhere on the board
/Wing_D6: J2.20; also elsewhere on the board
/Wing_D7: J2.21; also elsewhere on the board
/Wing_D8: J2.22; also elsewhere on the board
/Wing_D9: J2.23; also elsewhere on the board
/Wing_D10: J2.24; also elsewhere on the board
/Wing_D11: J2.25; also elsewhere on the board
/Wing_D12: J2.26; also elsewhere on the board
GND: J1.12, J1.30, J2.12, J2.30, J4.4; also elsewhere on the board

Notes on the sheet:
Piezo #

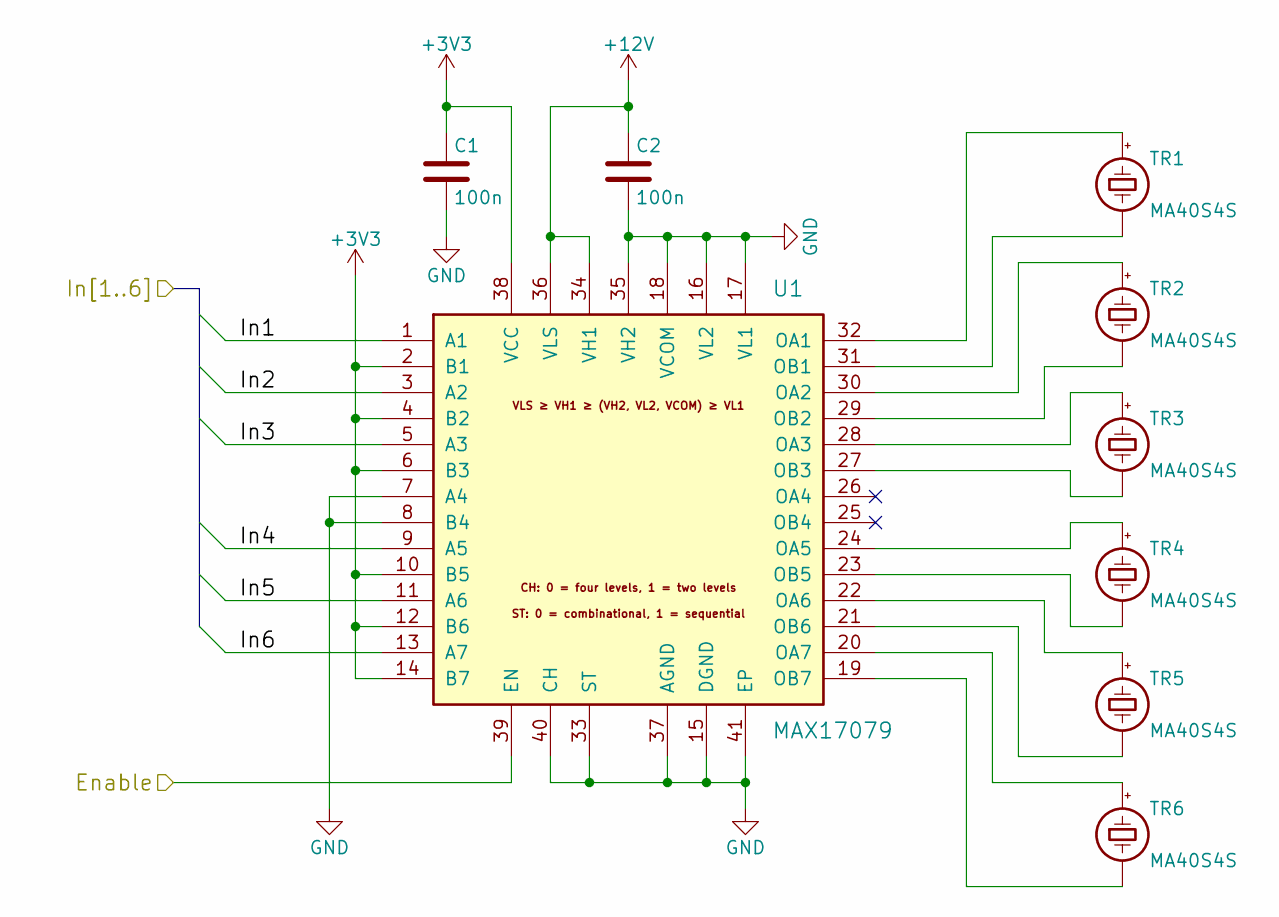
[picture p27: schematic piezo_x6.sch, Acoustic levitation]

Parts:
C1, C2: 100n; C_0805_HandSoldering; ManufacturerPartNumber 885012207072
TR1, TR2, TR3, TR4, TR5, TR6: MA40S4S; Murata_MA40S4S_TE_8134-HC-8P2; ManufacturerPartNumber MA40S4S
U1: MAX17079; QFN-40-1EP_6x6mm_Pitch0.5mm_HandSoldering; ManufacturerPartNumber MAX17079GTL+

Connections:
+3V3: C1.1, U1.2 (B1), U1.4 (B2), U1.6 (B3), U1.10 (B5), U1.12 (B6), U1.14 (B7), U1.38 (VCC); also elsewhere on the board
+12V: C2.1, U1.34 (VH1), U1.36 (VLS); also elsewhere on the board
/Enable: U1.39 (EN); also elsewhere on the board
/Piezo_A1: U1.1 (A1); also elsewhere on the board
/Piezo_A2: U1.3 (A2); also elsewhere on the board
/Piezo_A3: U1.5 (A3); also elsewhere on the board
/Piezo_A4: U1.9 (A5); also elsewhere on the board
/Piezo_A5: U1.11 (A6); also elsewhere on the board
/Piezo_A6: U1.13 (A7); also elsewhere on the board
GND: C1.2, C2.2, U1.7 (A4), U1.8 (B4), U1.15 (DGND), U1.16 (VL2), U1.17 (VL1), U1.18 (VCOM), U1.33 (ST), U1.35 (VH2), U1.37 (AGND), U1.40 (CH), U1.41 (EP); also elsewhere on the board
unnamed: TR1.1 (-), U1.31 (OB1)
unnamed: TR1.2 (+), U1.32 (OA1)
unnamed: TR2.1 (-), U1.29 (OB2)
unnamed: TR2.2 (+), U1.30 (OA2)
unnamed: TR3.1 (-), U1.27 (OB3)
unnamed: TR3.2 (+), U1.28 (OA3)
unnamed: TR4.1 (-), U1.23 (OB5)
unnamed: TR4.2 (+), U1.24 (OA5)
unnamed: TR5.1 (-), U1.21 (OB6)
unnamed: TR5.2 (+), U1.22 (OA6)
unnamed: TR6.1 (-), U1.19 (OB7)
unnamed: TR6.2 (+), U1.20 (OA7)

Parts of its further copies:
C3, C4, C5, C6, C7, C8, C9, C10, C11, C12: 100n; C_0805_HandSoldering; ManufacturerPartNumber 885012207072
TR7, TR8, TR9, TR10, TR11, TR12, TR13, TR14, TR15, TR16, TR17, TR18, TR19, TR20, TR21, TR22, TR23, TR24, TR25, TR26, TR27, TR28, TR29, TR30, TR31, TR32, TR33, TR34, TR35, TR36: MA40S4S; Murata_MA40S4S_TE_8134-HC-8P2; ManufacturerPartNumber MA40S4S
U2, U3, U4, U5, U6: MAX17079; QFN-40-1EP_6x6mm_Pitch0.5mm_HandSoldering; ManufacturerPartNumber MAX17079GTL+

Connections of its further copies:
+3V3: C3.1, C5.1, C7.1, C9.1, C11.1, U2.2 (B1), U2.4 (B2), U2.6 (B3), U2.10 (B5), U2.12 (B6), U2.14 (B7), U2.38 (VCC), U3.2 (B1), U3.4 (B2), U3.6 (B3), U3.10 (B5), U3.12 (B6), U3.14 (B7), U3.38 (VCC), U4.2 (B1), U4.4 (B2), U4.6 (B3), U4.10 (B5), U4.12 (B6), U4.14 (B7), U4.38 (VCC), U5.2 (B1), U5.4 (B2), U5.6 (B3), U5.10 (B5), U5.12 (B6), U5.14 (B7), U5.38 (VCC), U6.2 (B1), U6.4 (B2), U6.6 (B3), U6.10 (B5), U6.12 (B6), U6.14 (B7), U6.38 (VCC); also elsewhere on the board
+12V: C4.1, C6.1, C8.1, C10.1, C12.1, U2.34 (VH1), U2.36 (VLS), U3.34 (VH1), U3.36 (VLS), U4.34 (VH1), U4.36 (VLS), U5.34 (VH1), U5.36 (VLS), U6.34 (VH1), U6.36 (VLS); also elsewhere on the board
/Enable: U2.39 (EN), U3.39 (EN), U4.39 (EN), U5.39 (EN), U6.39 (EN); also elsewhere on the board
/Piezo_B1: U2.1 (A1); also elsewhere on the board
/Piezo_B2: U2.3 (A2); also elsewhere on the board
/Piezo_B3: U2.5 (A3); also elsewhere on the board
/Piezo_B4: U2.9 (A5); also elsewhere on the board
/Piezo_B5: U2.11 (A6); also elsewhere on the board
/Piezo_B6: U2.13 (A7); also elsewhere on the board
/Piezo_C1: U3.1 (A1); also elsewhere on the board
/Piezo_C2: U3.3 (A2); also elsewhere on the board
/Piezo_C3: U3.5 (A3); also elsewhere on the board
/Piezo_C4: U3.9 (A5); also elsewhere on the board
/Piezo_C5: U3.11 (A6); also elsewhere on the board
/Piezo_C6: U3.13 (A7); also elsewhere on the board
/Piezo_D1: U4.1 (A1); also elsewhere on the board
/Piezo_D2: U4.3 (A2); also elsewhere on the board
/Piezo_D3: U4.5 (A3); also elsewhere on the board
/Piezo_D4: U4.9 (A5); also elsewhere on the board
/Piezo_D5: U4.11 (A6); also elsewhere on the board
/Piezo_D6: U4.13 (A7); also elsewhere on the board
/Piezo_E1: U5.1 (A1); also elsewhere on the board
/Piezo_E2: U5.3 (A2); also elsewhere on the board
/Piezo_E3: U5.5 (A3); also elsewhere on the board
/Piezo_E4: U5.9 (A5); also elsewhere on the board
/Piezo_E5: U5.11 (A6); also elsewhere on the board
/Piezo_E6: U5.13 (A7); also elsewhere on the board
/Piezo_F1: U6.1 (A1); also elsewhere on the board
/Piezo_F2: U6.3 (A2); also elsewhere on the board
/Piezo_F3: U6.5 (A3); also elsewhere on the board
/Piezo_F4: U6.9 (A5); also elsewhere on the board
/Piezo_F5: U6.11 (A6); also elsewhere on the board
/Piezo_F6: U6.13 (A7); also elsewhere on the board
GND: C3.2, C4.2, C5.2, C6.2, C7.2, C8.2, C9.2, C10.2, C11.2, C12.2, U2.7 (A4), U2.8 (B4), U2.15 (DGND), U2.16 (VL2), U2.17 (VL1), U2.18 (VCOM), U2.33 (ST), U2.35 (VH2), U2.37 (AGND), U2.40 (CH), U2.41 (EP), U3.7 (A4), U3.8 (B4), U3.15 (DGND), U3.16 (VL2), U3.17 (VL1), U3.18 (VCOM), U3.33 (ST), U3.35 (VH2), U3.37 (AGND), U3.40 (CH), U3.41 (EP), U4.7 (A4), U4.8 (B4), U4.15 (DGND), U4.16 (VL2), U4.17 (VL1), U4.18 (VCOM), U4.33 (ST), U4.35 (VH2), U4.37 (AGND), U4.40 (CH), U4.41 (EP), U5.7 (A4), U5.8 (B4), U5.15 (DGND), U5.16 (VL2), U5.17 (VL1), U5.18 (VCOM), U5.33 (ST), U5.35 (VH2), U5.37 (AGND), U5.40 (CH), U5.41 (EP), U6.7 (A4), U6.8 (B4), U6.15 (DGND), U6.16 (VL2), U6.17 (VL1), U6.18 (VCOM), U6.33 (ST), U6.35 (VH2), U6.37 (AGND), U6.40 (CH), U6.41 (EP); also elsewhere on the board
unnamed: TR7.1 (-), U2.31 (OB1)
unnamed: TR7.2 (+), U2.32 (OA1)
unnamed: TR8.1 (-), U2.29 (OB2)
unnamed: TR8.2 (+), U2.30 (OA2)
unnamed: TR9.1 (-), U2.27 (OB3)
unnamed: TR9.2 (+), U2.28 (OA3)
unnamed: TR10.1 (-), U2.23 (OB5)
unnamed: TR10.2 (+), U2.24 (OA5)
unnamed: TR11.1 (-), U2.21 (OB6)
unnamed: TR11.2 (+), U2.22 (OA6)
unnamed: TR12.1 (-), U2.19 (OB7)
unnamed: TR12.2 (+), U2.20 (OA7)
unnamed: TR13.1 (-), U3.31 (OB1)
unnamed: TR13.2 (+), U3.32 (OA1)
unnamed: TR14.1 (-), U3.29 (OB2)
unnamed: TR14.2 (+), U3.30 (OA2)
unnamed: TR15.1 (-), U3.27 (OB3)
unnamed: TR15.2 (+), U3.28 (OA3)
unnamed: TR16.1 (-), U3.23 (OB5)
unnamed: TR16.2 (+), U3.24 (OA5)
unnamed: TR17.1 (-), U3.21 (OB6)
unnamed: TR17.2 (+), U3.22 (OA6)
unnamed: TR18.1 (-), U3.19 (OB7)
unnamed: TR18.2 (+), U3.20 (OA7)
unnamed: TR19.1 (-), U4.31 (OB1)
unnamed: TR19.2 (+), U4.32 (OA1)
unnamed: TR20.1 (-), U4.29 (OB2)
unnamed: TR20.2 (+), U4.30 (OA2)
unnamed: TR21.1 (-), U4.27 (OB3)
unnamed: TR21.2 (+), U4.28 (OA3)
unnamed: TR22.1 (-), U4.23 (OB5)
unnamed: TR22.2 (+), U4.24 (OA5)
unnamed: TR23.1 (-), U4.21 (OB6)
unnamed: TR23.2 (+), U4.22 (OA6)
unnamed: TR24.1 (-), U4.19 (OB7)
unnamed: TR24.2 (+), U4.20 (OA7)
unnamed: TR25.1 (-), U5.31 (OB1)
unnamed: TR25.2 (+), U5.32 (OA1)
unnamed: TR26.1 (-), U5.29 (OB2)
unnamed: TR26.2 (+), U5.30 (OA2)
unnamed: TR27.1 (-), U5.27 (OB3)
unnamed: TR27.2 (+), U5.28 (OA3)
unnamed: TR28.1 (-), U5.23 (OB5)
unnamed: TR28.2 (+), U5.24 (OA5)
unnamed: TR29.1 (-), U5.21 (OB6)
unnamed: TR29.2 (+), U5.22 (OA6)
unnamed: TR30.1 (-), U5.19 (OB7)
unnamed: TR30.2 (+), U5.20 (OA7)
unnamed: TR31.1 (-), U6.31 (OB1)
unnamed: TR31.2 (+), U6.32 (OA1)
unnamed: TR32.1 (-), U6.29 (OB2)
unnamed: TR32.2 (+), U6.30 (OA2)
unnamed: TR33.1 (-), U6.27 (OB3)
unnamed: TR33.2 (+), U6.28 (OA3)
unnamed: TR34.1 (-), U6.23 (OB5)
unnamed: TR34.2 (+), U6.24 (OA5)
unnamed: TR35.1 (-), U6.21 (OB6)
unnamed: TR35.2 (+), U6.22 (OA6)
unnamed: TR36.1 (-), U6.19 (OB7)
unnamed: TR36.2 (+), U6.20 (OA7)

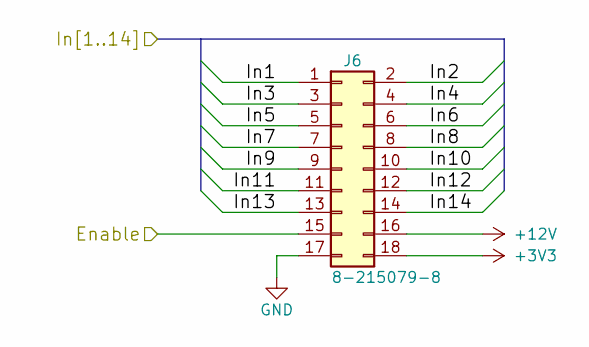
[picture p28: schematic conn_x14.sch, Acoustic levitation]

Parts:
J6: 8-215079-8; TE_8-215079-8; ManufacturerPartNumber 8-215079-8

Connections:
+3V3: J6.18; also elsewhere on the board
+12V: J6.16; also elsewhere on the board
/Enable: J6.15; also elsewhere on the board
/Wing_A1: J6.1; also elsewhere on the board
/Wing_A2: J6.2; also elsewhere on the board
/Wing_A3: J6.3; also elsewhere on the board
/Wing_A4: J6.4; also elsewhere on the board
/Wing_A5: J6.5; also elsewhere on the board
/Wing_A6: J6.6; also elsewhere on the board
/Wing_A7: J6.7; also elsewhere on the board
/Wing_A8: J6.8; also elsewhere on the board
/Wing_A9: J6.9; also elsewhere on the board
/Wing_A10: J6.10; also elsewhere on the board
/Wing_A11: J6.11; also elsewhere on the board
/Wing_A12: J6.12; also elsewhere on the board
/Wing_A13: J6.13; also elsewhere on the board
/Wing_A14: J6.14; also elsewhere on the board
GND: J6.17; also elsewhere on the board

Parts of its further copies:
J7, J8, J9: 8-215079-8; TE_8-215079-8; ManufacturerPartNumber 8-215079-8

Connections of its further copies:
+3V3: J7.18, J8.18, J9.18; also elsewhere on the board
+12V: J7.16, J8.16, J9.16; also elsewhere on the board
/Enable: J7.15, J8.15, J9.15; also elsewhere on the board
/Wing_A13: J7.14; also elsewhere on the board
/Wing_A14: J9.13; also elsewhere on the board
/Wing_B1: J7.1; also elsewhere on the board
/Wing_B2: J7.2; also elsewhere on the board
/Wing_B3: J7.3; also elsewhere on the board
/Wing_B4: J7.4; also elsewhere on the board
/Wing_B5: J7.5; also elsewhere on the board
/Wing_B6: J7.6; also elsewhere on the board
/Wing_B7: J7.7; also elsewhere on the board
/Wing_B8: J7.8; also elsewhere on the board
/Wing_B9: J7.9; also elsewhere on the board
/Wing_B10: J7.10; also elsewhere on the board
/Wing_B11: J7.11; also elsewhere on the board
/Wing_B12: J7.12; also elsewhere on the board
/Wing_B13: J7.13, J8.14; also elsewhere on the board
/Wing_C1: J8.1; also elsewhere on the board
/Wing_C2: J8.2; also elsewhere on the board
/Wing_C3: J8.3; also elsewhere on the board
/Wing_C4: J8.4; also elsewhere on the board
/Wing_C5: J8.5; also elsewhere on the board
/Wing_C6: J8.6; also elsewhere on the board
/Wing_C7: J8.7; also elsewhere on the board
/Wing_C8: J8.8; also elsewhere on the board
/Wing_C9: J8.9; also elsewhere on the board
/Wing_C10: J8.10; also elsewhere on the board
/Wing_C11: J8.11; also elsewhere on the board
/Wing_C12: J8.12; also elsewhere on the board
/Wing_C13: J8.13, J9.14; also elsewhere on the board
/Wing_D1: J9.1; also elsewhere on the board
/Wing_D2: J9.2; also elsewhere on the board
/Wing_D3: J9.3; also elsewhere on the board
/Wing_D4: J9.4; also elsewhere on the board
/Wing_D5: J9.5; also elsewhere on the board
/Wing_D6: J9.6; also elsewhere on the board
/Wing_D7: J9.7; also elsewhere on the board
/Wing_D8: J9.8; also elsewhere on the board
/Wing_D9: J9.9; also elsewhere on the board
/Wing_D10: J9.10; also elsewhere on the board
/Wing_D11: J9.11; also elsewhere on the board
/Wing_D12: J9.12; also elsewhere on the board
GND: J7.17, J8.17, J9.17; also elsewhere on the board

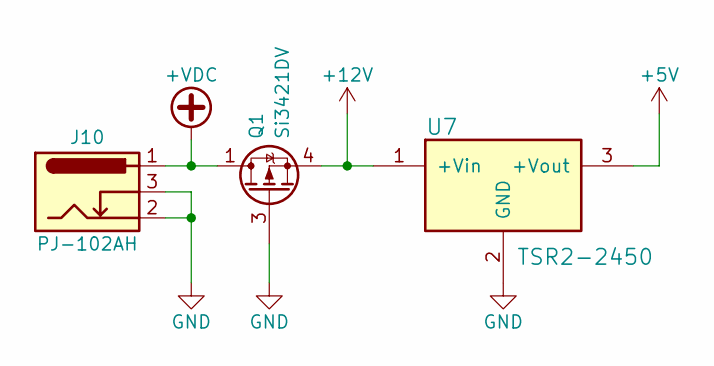
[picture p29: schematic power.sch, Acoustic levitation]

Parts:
J10: PJ-102AH; CUI_PJ-102AH; ManufacturerPartNumber PJ-102AH
Q1: Si3421DV; TSOP-6_2.9x1.5mm_Pitch0.95mm; ManufacturerPartNumber SI3421DV-T1-GE3
U7: TSR2-2450; Traco_TSR2; ManufacturerPartNumber TSR 2-2450

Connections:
+5V: U7.3 (+Vout); also elsewhere on the board
+12V: Q1.4 (S), U7.1 (+Vin); also elsewhere on the board
+VDC: J10.1, Q1.1 (D), Q1.2 (D), Q1.5 (D), Q1.6 (D)
GND: J10.2, J10.3, Q1.3 (G), U7.2 (GND); also elsewhere on the board

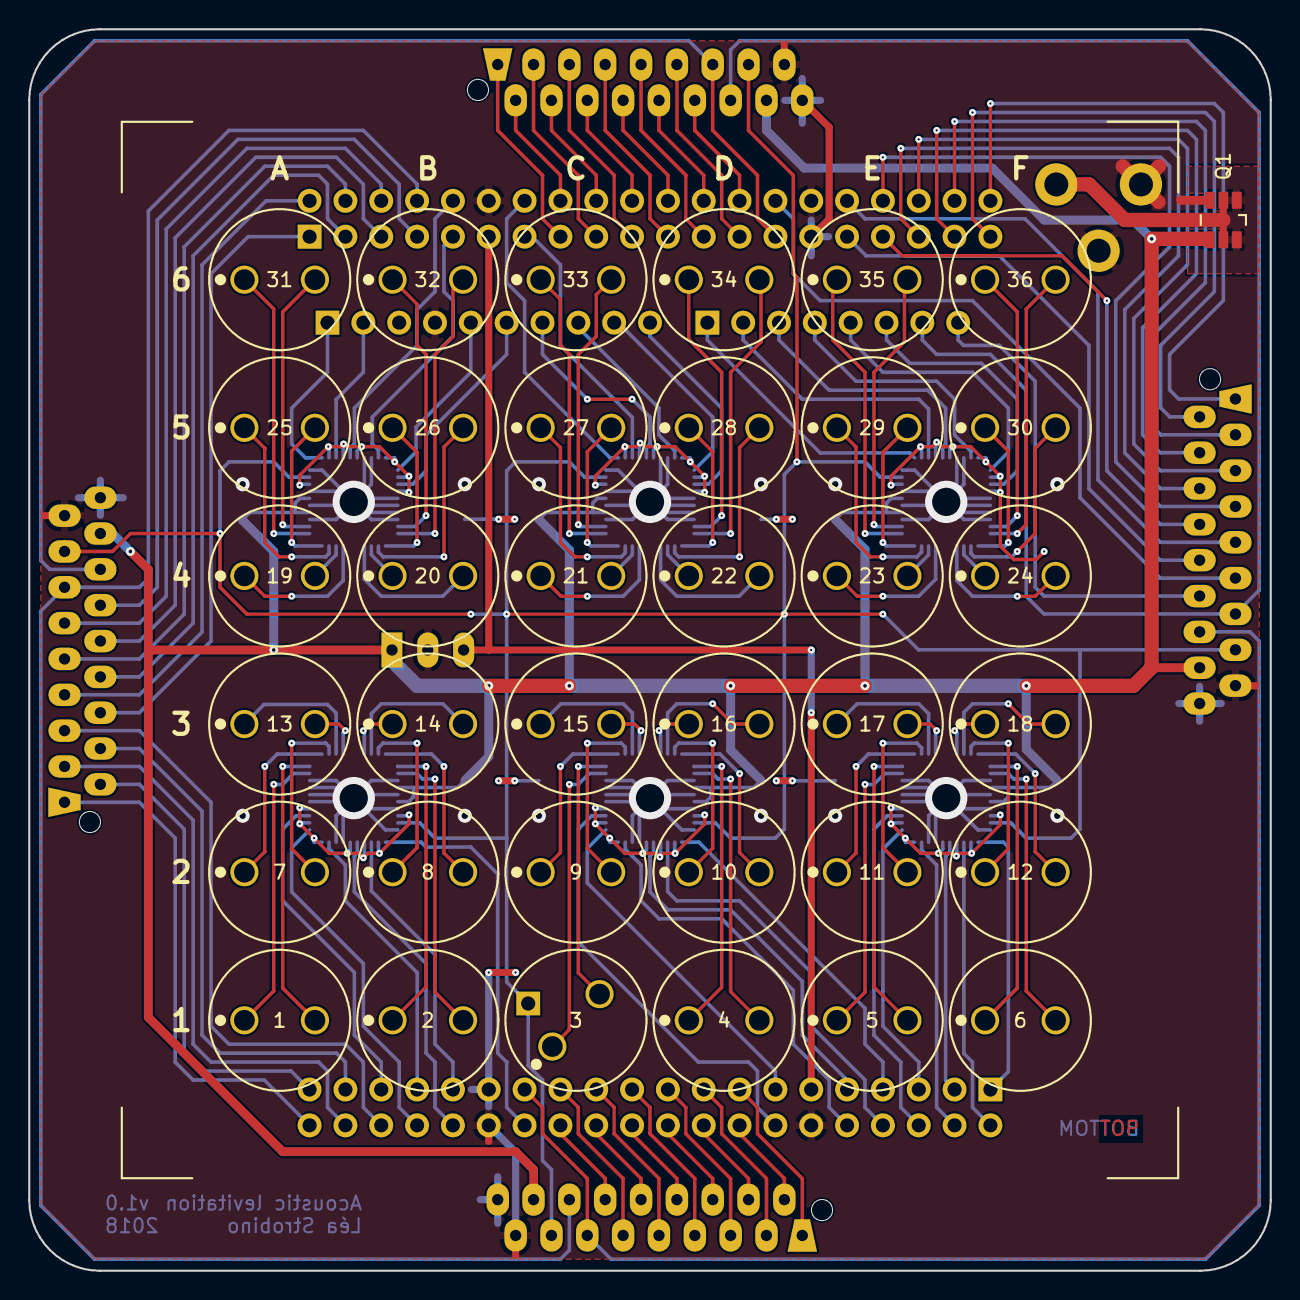
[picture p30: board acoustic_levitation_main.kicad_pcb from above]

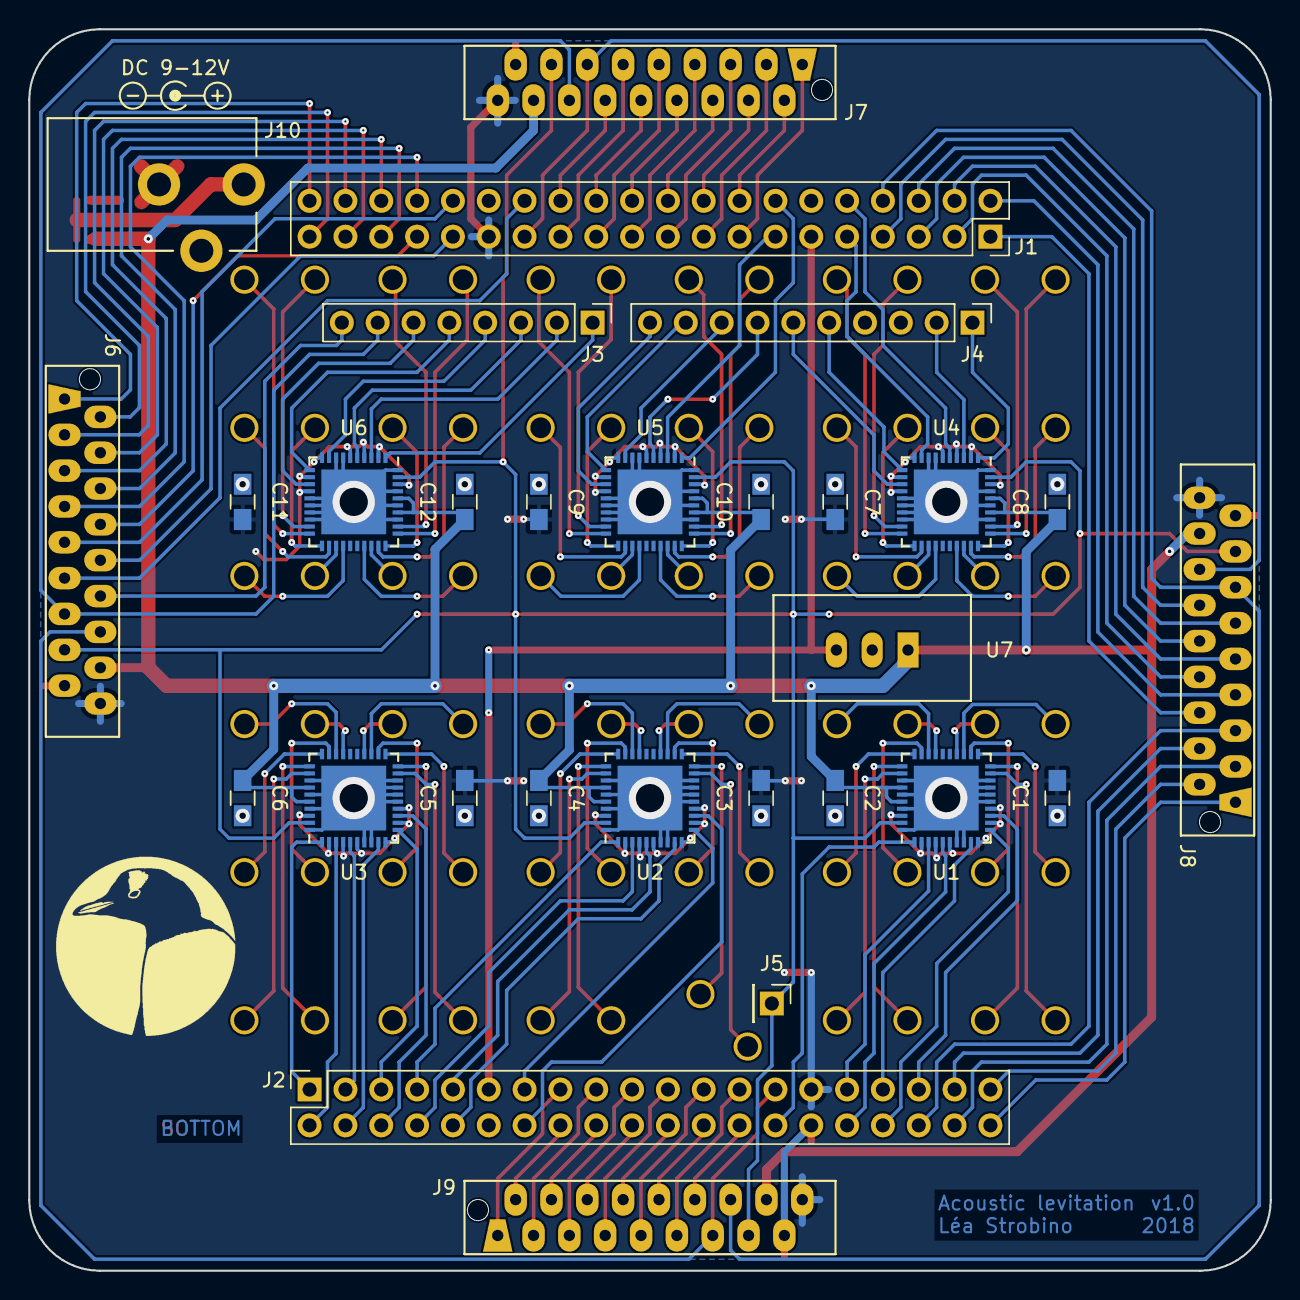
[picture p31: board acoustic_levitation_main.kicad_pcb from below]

Board: 2 copper layers, 88.0 x 88.0 mm, 66 parts (29 on the bottom side), 166 nets.

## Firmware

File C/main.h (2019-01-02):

/*
 * main.h
 *
 * Author       : Léa Strobino
 * Revision     : 1.0
 * Last updated : Sat, 02 Jun 2018 11:04:22 +0200
 * 
 * Copyright Léa Strobino, 2018
 * Licensed under the CERN OHL v1.2
 * 
 * You may redistribute and modify this file under the terms of the CERN OHL
 * v1.2. (http://ohwr.org/cernohl). This file is distributed WITHOUT ANY EXPRESS
 * OR IMPLIED WARRANTY, INCLUDING OF MERCHANTABILITY, SATISFACTORY QUALITY AND
 * FITNESS FOR A PARTICULAR PURPOSE.
 * Please see the CERN OHL v1.2 for applicable conditions.
 */

#ifndef MAIN_H_
#define MAIN_H_

#include <stdint.h>
#include "trap.h"

#define DEFAULT_X   0 // mm
#define DEFAULT_Y   0 // mm
#define DEFAULT_Z  20 // mm
#define DEFAULT_V  20 // mm/s

#define DEFAULT_VORTEX_HELICITY    1
#define DEFAULT_TWIN_ANGLE         0 // rad
#define DEFAULT_BOTTLE_RADIUS     10 // mm
#define DEFAULT_N                200 // 40 kHz / (200+200) = 100 Hz

#define LED_VORTEX  2
#define LED_TWIN    1
#define LED_BOTTLE  3

#define ANSI_ED  "\33[2J\33[H"
#define ANSI_EL  "\33[2K\r"

#define GCODE "GgMmFfSsTtXxYyZzUuVvWwRr"

typedef enum {
  VORTEX,
  TWIN,
  BOTTLE
} trap_t;

int main(int argc, char *argv[]);
void get_piezo_conf(const char *file);
void set_phase_zero();
void set_trap_vortex(point_t p, uint8_t helicity);
void set_trap_twin(point_t p, double angle);
void set_trap_bottle(point_t p, double radius);
void move(point_t *p, point_t q, double velocity);
void print_info(point_t p, double velocity);
void cleanup();
void init_signal();
void handle_signal(int sig);
char *strword(char **stringp);

#endif /* MAIN_H_ */

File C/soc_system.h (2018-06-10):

#ifndef _ALTERA_SOC_SYSTEM_H_
#define _ALTERA_SOC_SYSTEM_H_

/*
 * This file was automatically generated by the swinfo2header utility.
 * 
 * Created from SOPC Builder system 'soc_system' in
 * file 'soc_system.sopcinfo'.
 */

/*
 * This file contains macros for module 'hps_0' and devices
 * connected to the following master:
 *   h2f_lw_axi_master
 * 
 * Do not include this header file and another header file created for a
 * different module or master group at the same time.
 * Doing so may result in duplicate macro names.
 * Instead, use the system header file which has macros with unique names.
 */

/*
 * Macros for device 'piezo_controller_0', class 'piezo_controller'
 * The macros are prefixed with 'PIEZO_CONTROLLER_0_'.
 * The prefix is the slave descriptor.
 */
#define PIEZO_CONTROLLER_0_COMPONENT_TYPE piezo_controller
#define PIEZO_CONTROLLER_0_COMPONENT_NAME piezo_controller_0
#define PIEZO_CONTROLLER_0_BASE 0x0
#define PIEZO_CONTROLLER_0_SPAN 512
#define PIEZO_CONTROLLER_0_END 0x1ff
#define PIEZO_CONTROLLER_0_ENABLE_REG_OFST 0x0
#define PIEZO_CONTROLLER_0_FREQ 50000000
#define PIEZO_CONTROLLER_0_PERIOD_REG_OFST 0x2
#define PIEZO_CONTROLLER_0_PHASE_A_COUNT_REG_OFST 0x4
#define PIEZO_CONTROLLER_0_PHASE_A_REG_OFST 0x20
#define PIEZO_CONTROLLER_0_PHASE_B_COUNT_REG_OFST 0x6
#define PIEZO_CONTROLLER_0_PHASE_B_REG_OFST 0x110
#define PIEZO_CONTROLLER_0_PIEZO_COUNT 89

/*
 * Macros for device 'fpga_led', class 'altera_avalon_pio'
 * The macros are prefixed with 'FPGA_LED_'.
 * The prefix is the slave descriptor.
 */
#define FPGA_LED_COMPONENT_TYPE altera_avalon_pio
#define FPGA_LED_COMPONENT_NAME fpga_led
#define FPGA_LED_BASE 0x200
#define FPGA_LED_SPAN 32
#define FPGA_LED_END 0x21f
#define FPGA_LED_BIT_CLEARING_EDGE_REGISTER 0
#define FPGA_LED_BIT_MODIFYING_OUTPUT_REGISTER 1
#define FPGA_LED_CAPTURE 0
#define FPGA_LED_DATA_WIDTH 8
#define FPGA_LED_DO_TEST_BENCH_WIRING 0
#define FPGA_LED_DRIVEN_SIM_VALUE 0
#define FPGA_LED_EDGE_TYPE NONE
#define FPGA_LED_FREQ 50000000
#define FPGA_LED_HAS_IN 0
#define FPGA_LED_HAS_OUT 1
#define FPGA_LED_HAS_TRI 0
#define FPGA_LED_IRQ_TYPE NONE
#define FPGA_LED_RESET_VALUE 0

/*
 * Macros for device 'fpga_key', class 'altera_avalon_pio'
 * The macros are prefixed with 'FPGA_KEY_'.
 * The prefix is the slave descriptor.
 */
#define FPGA_KEY_COMPONENT_TYPE altera_avalon_pio
#define FPGA_KEY_COMPONENT_NAME fpga_key
#define FPGA_KEY_BASE 0x220
#define FPGA_KEY_SPAN 16
#define FPGA_KEY_END 0x22f
#define FPGA_KEY_IRQ 0
#define FPGA_KEY_BIT_CLEARING_EDGE_REGISTER 1
#define FPGA_KEY_BIT_MODIFYING_OUTPUT_REGISTER 0
#define FPGA_KEY_CAPTURE 1
#define FPGA_KEY_DATA_WIDTH 2
#define FPGA_KEY_DO_TEST_BENCH_WIRING 0
#define FPGA_KEY_DRIVEN_SIM_VALUE 0
#define FPGA_KEY_EDGE_TYPE FALLING
#define FPGA_KEY_FREQ 50000000
#define FPGA_KEY_HAS_IN 1
#define FPGA_KEY_HAS_OUT 0
#define FPGA_KEY_HAS_TRI 0
#define FPGA_KEY_IRQ_TYPE EDGE
#define FPGA_KEY_RESET_VALUE 0


#endif /* _ALTERA_SOC_SYSTEM_H_ */

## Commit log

2018-06-03 Added PCB
    [acoustic_levitation_main.kicad_pcb, acoustic_levitation_main.sch, acoustic_levitation_main_bom.csv, acoustic_levitation_wing.kicad_pcb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]
2018-06-10 Added C
    [transducers.csv]
2018-06-15 Added LED & buttons assignments
2018-11-04 Upgraded PCB to KiCad 5
    [acoustic_levitation_main.kicad_pcb, acoustic_levitation_main.sch, acoustic_levitation_main_bom.csv, acoustic_levitation_wing.kicad_pcb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]
2019-01-02 Added license
    [acoustic_levitation_main.kicad_pcb, acoustic_levitation_main.sch, acoustic_levitation_wing.kicad_pcb, acoustic_levitation_wing.sch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]

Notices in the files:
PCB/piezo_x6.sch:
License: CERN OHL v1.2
